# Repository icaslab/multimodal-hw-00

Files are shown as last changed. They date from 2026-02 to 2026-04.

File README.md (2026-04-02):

⚔️ Work in Progress: This repository is under active development. Please do not make changes. ⚔️

### Multimodal Transcutaneous Monitor Hardware (PtcO₂ / PtcCO₂ / SpO₂ / BIA)

### Key Specs
- **MCU:** STM32WB55RGV6 (dual-core Cortex-M4/M0+, BLE 5.0) — VFQFPN68
- **Analog Front End:** ADPD7000 (optical + bio-impedance/BIA sensing) — 36-ball WLCSP, 0.4mm pitch
- **Storage:** S25FL512S — 512 Mb QuadSPI Flash (5×5 BGA)
- **Power Input:** USB-C (2.0) or 3.7V Li-Po with integrated battery charging

### Sensors / Peripherals
- **BME280** (Temp/Humidity/Pressure) over I²C (`0x76`)
- **ADXL367** (Accelerometer) over I²C (`0x53`)

### Power Management
- **MAX20345** single-chip PMIC (WLP-56, 0.4mm pitch) with:
  - Integrated Li-Po charger (ISET = 10kΩ → ~200mA charge current)
  - NTC thermistor monitoring (SEMITEC 103AT-11)
  - **Buck 2:** 1.8V analog rail (`1V8A`) — low-noise AFE supply
  - **Buck 3:** 3.3V digital rail (`3V3D`) — MCU + digital peripherals
  - **Buck-Boost:** 5.0V LED drive domain (`5V_LED`) — optical front end
  - **LDO 1:** 1.8V digital rail (`1V8D`)
  - **LDO 2:** 3.3V LED rail (`3V3_LED`)
  - **LDO 3:** Alternative output (`L3OUT`)
  - **Load Switches:** LSW1, LSW2 not used either 
  - Buck 1 unused — disabled via I²C

### PCB
- **Stackup:** 6-layer HDI (Sig+Pwr / GND / Sig / PwR / GND / Sig)
- **HDI:** Stacked/staggered µVias (100µm laser drill, 250µm pad, via-in-pad with epoxy fill + cap plating)

### Repository Organization
- `Datasheets/`  
  - Find component datasheets here.

### Schematic Sheets
- `00-multimodal-coversheet.SchDoc`
- `01-multimodal-powersupply.SchDoc`
- `04-multimodal-flash.SchDoc`
- `05-multimodal-analogfrontend.SchDoc`
- `06-multimodal-analogfrontend-PPG.SchDoc`
- `07-multimodal-microcontroller.SchDoc`
- `08-multimodal-microcontroller-oscillators.SchDoc`
- `10-multimodal-microcontroller-rf.SchDoc`
- `11-multimodal-combined-sensor.SchDoc`
- `12-multimodal-accelerometer.SchDoc`
- `13-multimodal-connections.SchDoc`

```text
⠀⠀⢸⡿⢦⣄⠀⢀⣠⣴⣶⠀⠀⠀⠀⠀⠀⠀⠀⠀⠀⠀⠀⠀⠀
⠀⠀⠘⣷⠀⠉⠛⠛⠉⢰⡇⠀⠀⠘⣷⣦⣾⡇⠀⠀⠀⠀⠀⠀⠀
⠀⢀⣰⠿⠀⠀⠀⠀⠀⢿⡁⠀⢀⣴⣿⣿⣿⣶⡄⠀⠀⠀⠀⠀⠀
⣴⣿⣁⡀⠀⠀⠀⠀⠀⠀⠻⣦⡀⠀⠀⢿⠃⠀⢀⣤⡀⠀⠀⠀⠀
⠀⠈⠉⠛⣿⡀⠀⣰⠟⠛⠛⠛⠛⠀⠀⠀⠀⣠⡾⢻⡇⠀⠀⠀⠀
⠀⠀⠀⠀⠈⣷⣼⠏⠀⠀⠀⢻⣟⠻⠿⢶⡾⠋⠀⢸⡇⠀⠀⠀⠀
⠀⠀⠀⠀⠀⠘⠃⠀⣴⠀⠀⠈⢻⣆⠀⠀⠀⠀⠀⠀⠻⢶⣤⣀⠀
⠀⠀⠀⠀⠀⠘⢷⣾⣿⣤⣄⠀⢈⣿⠀⠀⠀⠀⠀⠀⠀⢀⣉⣿⠿
⠀⠀⠀⠀⠀⢀⣾⠿⣿⡏⠉⢠⣾⠃⠀⠀⠀⠀⠀⢀⣾⠛⠋⠁⠀
⠀⠀⠀⠀⠀⠀⠀⠀⠙⠃⠀⣿⡷⠿⠟⠛⢿⣦⡀⢸⡇⠀⠀⠀⠀
⠀⠀⠀⠀⠀⠀⠀⠀⠀⠀⠀⠀⠀⠀⠀⠀⠀⠀⠀⠙⢿⣿⠃⠀⠀
⠀⠀⠀⠀⠀⠀⠀⠀⠀⠀⠀⠀⠀⠀⠀⠀⠀⠀⠀⠀⠀⠉⠀⠀⠀
```

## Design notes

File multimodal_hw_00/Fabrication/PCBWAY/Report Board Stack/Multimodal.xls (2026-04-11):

Board Stack Report
Stack Up |  | Layer Stack
Layer | Board Layer Stack | Name | Material | Thickness | Constant | Dk
1 |  | Top Overlay |  | 0mil
2 |  | Top Solder | Solder Resist | 0.4mil | 3.5 | 3.5
3 |  | L1_TOP | CF-001 | 0.689mil
4 |  | Dielectric 2 | PP-006 | 4.705mil | 4.45 | 4.45
5 |  | L2_GND | CF-004 | 1.378mil
6 |  | Dielectric 4 | PP-006 | 9.055mil | 4.6 | 4.6
7 |  | L3_Signal | CF-004 | 1.378mil
8 |  | Dielectric 6 | PP-006 | 5.118mil | 4.45 | 4.45
9 |  | Dielectric 1 | FR-4 | 0mil | 4.45 | 4.45
10 |  | Dielectric 7 | PP-006 | 5.118mil | 4.45 | 4.45
11 |  | L4_PWR | CF-004 | 1.378mil
12 |  | Dielectric 5 | PP-006 | 9.055mil | 4.6 | 4.6
13 |  | L5_GND | CF-004 | 1.378mil
14 |  | Dielectric 3 | PP-006 | 4.705mil | 4.45 | 4.45
15 |  | L6_BOTTOM | CF-001 | 0.689mil
16 |  | Bottom Solder | Solder Resist | 0.4mil | 3.5 | 3.5
17 |  | Bottom Overlay |  | 0mil
 | Height : 45.446mil

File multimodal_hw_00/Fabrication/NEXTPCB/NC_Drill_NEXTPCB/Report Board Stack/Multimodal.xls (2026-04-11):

Board Stack Report
Stack Up |  | Layer Stack
Layer | Board Layer Stack | Name | Material | Thickness | Constant | Dk
1 |  | Top Overlay |  | 0mil
2 |  | Top Solder | Solder Resist | 0.4mil | 3.5 | 3.5
3 |  | L1_TOP | CF-001 | 0.453mil
4 |  | Dielectric 2 | PP-006 | 3.032mil | 4 | 4
5 |  | L2_GND | CF-004 | 0.453mil
6 |  | Dielectric 4 | PP-006 | 3.032mil | 4 | 4
7 |  | L3_Signal | CF-004 | 0.453mil
8 |  | Dielectric 1 | FR-4 | 46.339mil | 4 | 4
9 |  | L4_PWR | CF-004 | 0.453mil
10 |  | Dielectric 5 | PP-006 | 3.032mil | 4 | 4
11 |  | L5_GND | CF-004 | 0.453mil
12 |  | Dielectric 3 | PP-006 | 3.032mil | 4 | 4
13 |  | L6_BOTTOM | CF-001 | 0.453mil
14 |  | Bottom Solder | Solder Resist | 0.4mil | 3.5 | 3.5
15 |  | Bottom Overlay |  | 0mil
 | Height : 61.985mil

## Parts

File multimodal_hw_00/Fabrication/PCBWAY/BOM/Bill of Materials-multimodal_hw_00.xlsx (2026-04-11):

Line # | Name | Description | Designator | Quantity | Manufacturer 1 | Manufacturer Part Number 1 | Manufacturer Lifecycle 1 | Supplier 1 | Supplier Part Number 1 | Supplier Unit Price 1 | Supplier Subtotal 1
 | ANT016008LCS2442MA2 | TDK - ANT016008LCS2442MA2 - Chip Antenna, ISM, 2.442 GHz, 50 Ohm, 1.6mm x 0.8mm x 0.4mm | AE1 | 1 | TDK | ANT016008LCS2442MA2 | Volume Production | DigiKey | 445-172405CT-ND | 0.61 | 0.61
 | C1005X5R1V105K050BC | CAP CER 1UF 35V X5R 0402 | C1, C8, C16, C18, C23, C24, C50 | 7 | TDK | C1005X5R1V105K050BC | Volume Production | DigiKey | 445-9073-1-ND | 0.071 | 0.71
 | C1005X5R1A475K050BC | CAP CER 4.7UF 10V X5R 0402 | C2, C38 | 2 | TDK | C1005X5R1A475K050BC | Volume Production | Digi-Key | 445-13820-1-ND
 | GRM188R61A226ME15D | CAP CER 22UF 10V X5R 0603 | C3, C4, C5, C9, C10, C13, C14 | 7 | Murata | GRM188R61A226ME15D | Volume Production | Avnet | GRM188R61A226ME15D | 0.01867 | 74.68
 | CL05A225KO5NQNC | CAP CER 2.2UF 16V X5R 0402 | C6, C11, C12, C15, C64 | 5 | Samsung Electro-Mechanics | CL05A225KO5NQNC | Volume Production | Avnet | CL05A225KO5NQNC | 0.0264 | 264
 | C1005X7R1H104K050BB | CAP CER 0.1UF 50V X7R 0402 | C7, C17, C26, C29, C30, C31, C33, C35, C36, C37, C40, C41, C42, C48, C51, C52, C53, C55, C57, C58, C60, C61 | 22 | TDK | C1005X7R1H104K050BB | Volume Production | DigiKey | 445-5932-1-ND | 0.041 | 0.902
 | GRM155R60J474KE19D | CAP CER 0.47UF 6.3V X5R 0402 | C21, C22, C25, C27 | 4 | Murata | GRM155R60J474KE19D | Not Recommended for New Design | Avnet | GRM155R60J474KE19D | 0.00818 | 81.8
 | 0402W106M6R3HI | CAP SMD,0402,X5R,10UF,20%,6.3V | C28, C32, C54, C56 | 4
 | GRM155R61A106ME11D | CAP CER 10UF 10V X5R 0402 | C34, C47, C49 | 3 | Murata | GRM155R61A106ME11D | Volume Production | DigiKey | 490-GRM155R61A106ME11DCT-ND | 0.013 | 0.13
 | CGA2B2C0G1H101J050BA | CAP CER 100PF 50V C0G 0402 | C43 | 1 | TDK | CGA2B2C0G1H101J050BA | Volume Production | DigiKey | 445-5596-1-ND | 0.1 | 0.1
 | CGA2B2C0G1H120J050BA | CAP CER 12PF 50V C0G 0402 | C45, C46 | 2 | TDK | CGA2B2C0G1H120J050BA | Volume Production | DigiKey | 445-5585-1-ND | 0.1 | 0.2
 | CGA2B2C0G1H101J050BA | CAP CER 100PF 50V C0G 0402 | C62 | 1 | TDK | CGA2B2C0G1H101J050BA | Volume Production | DigiKey | 445-5596-1-ND | 0.1 | 0.1
 | USBLC6-2SC6 | ESD Protection for USB 2.0 High Speed | CR1 | 1 | STMicroelectronics | USBLC6-2SC6 | Volume Production | Avnet | USBLC6-2SC6 | 0.07203 | 216.09
 | ESD9X5.0ST5G | TVS DIODE 5VWM 12.3VC SOD923 | CR3 | 1 | onsemi | ESD9X5.0ST5G | Volume Production | Avnet | ESD9X5.0ST5G | 0.01716 | 137.28
 | DESD3V3S1BL-7B | TVS DIODE 3.3V 7V DFN1006-2 | D1 | 1 | Diodes Inc. | DESD3V3S1BL-7B | Volume Production | DigiKey | DESD3V3S1BL-7BDICT-ND | 0.24 | 0.24
 | SFH 2703 | SENSOR PHOTODIODE 940NM 2SMD | D3, D10, D11 | 3 | Osram | SFH 2703 | Volume Production | Avnet | Q65112A8147 | 0.50312 | 1509.36
 | LXZ1-PR01 | LED LUXEON Z RYL BLUE 450NM 2SMD | D4, D5 | 2 | Lumileds | LXZ1-PR01 | Volume Production | DigiKey | 1416-1058-1-ND | 3.32 | 6.64
 | 019-141-411-R | PHOTODIODE RED MICRO SMT | D6 | 1 | Advanced Photonix | 019-141-411-R |  | DigiKey | 209-019-141-411-RCT-ND | 1.96 | 1.96
 | S15193 | PHOTODIODE PIN 380 NM-1000 NM 20V 0.64 A/W SMD | D7 | 1 |  |  |  | Hamamatsu
 | CT DBLP31.12-6C5D-56-J6Q4 | LED GREEN CLEAR SMD Green 536nm LED Indication - Discrete 2.3V 3-SMD, No Lead | D8 | 1 | Osram | CT DBLP31.12-6C5D-56-J6Q4 | Volume Production | Avnet | Q65112A4607
 | SFH 7015 | Multi-Color LEDs Red / IR LED 655nm / 940nm | D9 | 1 | Osram | SFH 7015 | Obsolete | Avnet | Q65113A4161 | 0.3798 | 1899
 | RB521S30T1G | DIODE SCHOTTKY 30V 200MA SOD523 | D12 | 1 |  |  |  | Hamamatsu
 | Orange | LED ORANGE CLEAR 0603 SMD | D13 | 1 | Lite-On | LTST-C191KFKT | Volume Production | DigiKey | 160-1445-1-ND | 0.11 | 0.11
 | MAF1608GAD601CT000 | FERRITE BEAD 120 OHM 0603 1LN | FB1, FB2, FB3, FB4 | 4 | TDK | MAF1608GAD601CT000 | Volume Production | Newark | MAF1608GAD601CT000 | 0.185 | 1.85
 | MFBA3V1608K-601-R | FERRITE BEAD 600 OHM 0603 1LN | FB5 | 1 | Eaton | MFBA3V1608K-601-R | Volume Production | DigiKey | 283-MFBA3V1608K-601-RCT-ND | 0.1 | 0.1
 | FTSH-105-01-F-DV-P-TR | Connector Header Surface Mount 10 position 0.050" (1.27mm) | J1 | 1
 | TH-Connector | Power Connector | J2 | 1
 | 2171790001 | Universal Serial Bus (USB) Shielded I/O Receptacle, Type C, Right-Angle, Top Mount, Surface Mount, Single Row, 16 Circuits, Gold (Au) Plating | J3 | 1
 | battery_connection |  | J4 | 1
 | U.FL-R-SMT(10) | CONN U.FL RCPT STR 50 OHM SMD | J5 | 1 | HIROSE ELECTRIC | U.FL-R-SMT(10) | Volume Production | DigiKey | H9161CT-ND | 1.29 | 1.29
 | electrode | one pad opening | J6, J7, J8, J9 | 4
 | SEMITEC 103AT-11 | NTC THERMISTOR 10KOHM 1% | J11 | 1
 | MLG0603P1N8CT000 | FIXED IND 1.8NH 700MA 100MOHM SM | L5 | 1 | TDK | MLG0603P1N8CT000 | Volume Production | DigiKey | 445-172430-1-ND | 0.1 | 0.1
 | MHQ0603P2N9ST000 | FIXED IND 2.9NH 450MA 300MOHM SM | L6 | 1 | TDK | MHQ0603P2N9ST000 | Volume Production | DigiKey | 445-16842-6-ND | 0.3 | 0.3
 | DFE201612E-2R2M=P2 | 2.2 µH Shielded Drum Core, Wirewound Inductor 1.8 A 116mOhm Max 0806 (2016 Metric) | L7, L9, L10 | 3
 | RMCF0402FT93K1 | RES 93.1K OHM 1% 1/16W 0402 | R1, R12 | 2 | Stackpole Electronics | RMCF0402FT93K1 | Volume Production | DigiKey | RMCF0402FT93K1CT-ND | 0.005 | 0.05
 | RMCF0402FT220K | RES 220K OHM 1% 1/16W 0402 | R2, R13 | 2 | Stackpole Electronics | RMCF0402FT220K | Volume Production | DigiKey | RMCF0402FT220KCT-ND | 0.005 | 0.05
 | RMCF0603ZT0R00 | RES 0 OHM JUMPER 1/10W 0603 | R3, R10, R17, R25, R34, R35, R39 | 7 | Stackpole Electronics | RMCF0603ZT0R00 | Volume Production | DigiKey | RMCF0603ZT0R00CT-ND | 0.006 | 0.06
 | RMCF0402FT100K | RES 100K OHM 1% 1/16W 0402 | R5, R8, R9, R15, R19, R24 | 6 | Stackpole Electronics | RMCF0402FT100K | Volume Production | DigiKey | RMCF0402FT100KCT-ND | 0.005 | 0.05
 | RMCF0402FT10K0 | RES 10K OHM 1% 1/16W 0402 | R6, R11 | 2 | Stackpole Electronics | RMCF0402FT10K0 | Volume Production | DigiKey | RMCF0402FT10K0CT-ND | 0.005 | 0.05
 | RMCF0603JG10K0 | RES 10K OHM 5% 1/10W 0603 | R7 | 1 | Stackpole Electronics | RMCF0603JG10K0 | Volume Production | DigiKey | 738-RMCF0603JG10K0CT-ND | 0.1 | 0.1
 | RMCF0603JG100K | RES 100K OHM 5% 1/10W 0603 | R21 | 1 | Stackpole Electronics | RMCF0603JG100K | Volume Production | DigiKey | RMCF0603JG100KCT-ND | 0.1 | 0.1
 | RMCF0402JT220R | RES 220 OHM 5% 1/16W 0402 | R22 | 1 | Stackpole Electronics | RMCF0402JT220R | Volume Production | DigiKey | RMCF0402JT220RCT-ND | 0.1 | 0.1
 | ERA-2AEB512X | RES SMD 5.1K OHM 0.1% 1/16W 0402 | R28, R33 | 2 | Panasonic | ERA2AEB512X | Volume Production | Arrow Electronics | ERA-2AEB512X | 0.0452 | 452
 | RMCF0402FT4K70 | RES 4.7K OHM 1% 1/16W 0402 | R31, R32 | 2 | Stackpole Electronics | RMCF0402FT4K70 | Volume Production | Digi-Key | RMCF0402FT4K70CT-ND
 | RMCF0402FT10R0 | RES 10 OHM 1% 1/16W 0402 | R36, R37 | 2 | Stackpole Electronics | RMCF0402FT10R0 | Volume Production | DigiKey | RMCF0402FT10R0CT-ND | 0.006 | 0.06
 | RMCF0402ZT0R00 | RES 0 OHM JUMPER 1/16W 0402 | R38 | 1 | Stackpole Electronics | RMCF0402ZT0R00 | Volume Production | DigiKey | RMCF0402ZT0R00CT-ND | 0.1 | 0.1
 | S0951-46R | RFI SHIELD CLIP MINI TIN SMD | SC1, SC2 | 2 | Harwin | S0951-46R | Volume Production | DigiKey | 952-2669-1-ND | 0.19 | 0.38
 | MS190-10C | RF SHLD COVER 0.563"X0.764" SNAP | SH1 | 1 | Masach Tech | MS190-10C | Volume Production | DigiKey | 2333-MS190-10C-ND | 1.12 | 1.12
 | NANOT 240 AS | SWITCH TACTILE SPST-NO 0.02A 15V | SW1, SW2 | 2 |  |  |  | Future Electronics | 2189518
 | MAX20345BEWN+T | PMIC with Ultra-Low IQ Voltage Regulators, Buck-Boost for Optical Sensing and Charger for Small Lithium Ion Systems | U1 | 1 | Analog Devices | MAX20345BEWN+T | Volume Production | DigiKey | 505-MAX20345BEWN+TTR-ND
 | S25FL512SAGBHEA10 | FLASH - NOR Memory IC 512Mbit SPI - Quad I/O 133 MHz 24-BGA (6x8) | U3 | 1
 | ADXL367BCCZ-RL7 | Accelerometer X, Y, Z Axis ±2g, 4g, 8g 6.25Hz ~ 200Hz 12-LGA (2.2x2.3) | U4 | 1 | Analog Devices | ADXL367BCCZ-RL7 | Volume Production | DigiKey | 505-ADXL367BCCZ-RL7CT-ND
 | ADPD7000BCBZR7 | Multimodal Sensor Front End | U5 | 1
 | STM32WB55RGV6 | Ultra-low-power dual core Arm Cortex-M4 MCU 64 MHz, Cortex-M0+ 32 MHz with 1 Mbyte of Flash memory, Bluetooth LE 5.4, 802.15.4, Zigbee, Thread, Matter, USB, LCD, AES-256 | U6 | 1
 | MLPF-WB55-01E3 | 2.4 GHz Matched filter companion chip for STM32WB55Cx and STM32WB55Rx | U7 | 1 | STMicroelectronics | MLPF-WB55-01E3 | Volume Production | DigiKey | 497-19088-1-ND | 0.37 | 0.37
 | BME280 | SENSOR PRESSURE HUMIDITY TEMP Humidity, Pressure, Temperature 0 ~ 100% RH I2C, SPI ±3% 1 s Surface Mount | U8 | 1
 | 32MHz | CRYSTAL 32MHZ 8PF 60R SMD | XO1 | 1 |  |  |  | Digi-Key | 644-1373-1-ND
 | ECS-327-9-12R-C-TR | Crystal 0.032768MHz ±10ppm (Tol) 9pF Flexural 70000Ohm Automotive 2-Pin Ultra Mini-CSMD T/R | XO2 | 1 | ECS International | ECS-.327-9-12R-C-TR | Volume Production | DigiKey | XC2744CT-ND | 0.75 | 0.75

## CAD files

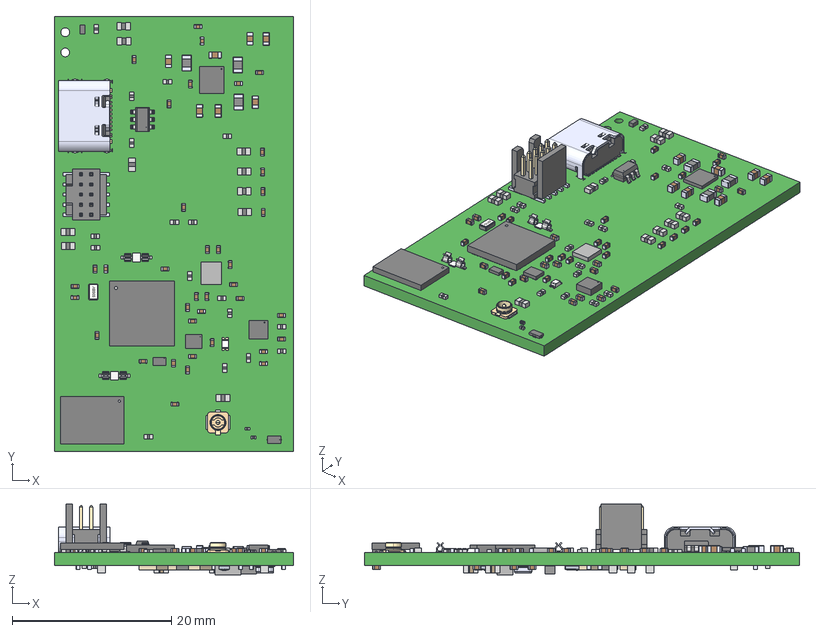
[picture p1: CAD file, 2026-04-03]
multimodal_hw_00/3D-board/Multimodal.step
30.0 x 54.6 x 8.87 mm
STA_RMCF0402_STP x 20
s0951-46 x 2
DFE201612E-2R2M=P2 x 3
bigPin x 2
Extruded x 2
ABS06-32.768KHZ-9-1-T--3DModel-STEP-400430
MLPF-WB55-01E3_STM
U.FL-R-SMT(10)--3DModel-STEP-56544
LTST-C191KRKT
CTDBLP3112-6C5D-56-J6Q4_OSR
Pins
LUXEON Z InGaN Direct Color 0660 x 2
SOT23-6L_STM
QFN_2442MA2_TDK

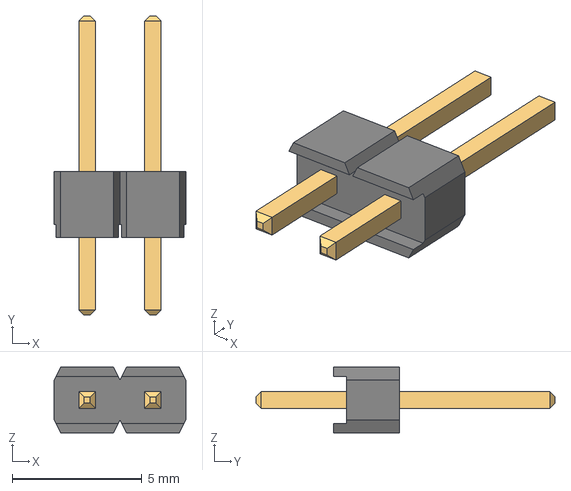
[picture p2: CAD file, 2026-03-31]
multimodal_hw_00/3D-models/STP_61300211121_rev1.stp
5.08 x 11.5 x 2.54 mm
6130xx11121_PIN x 2

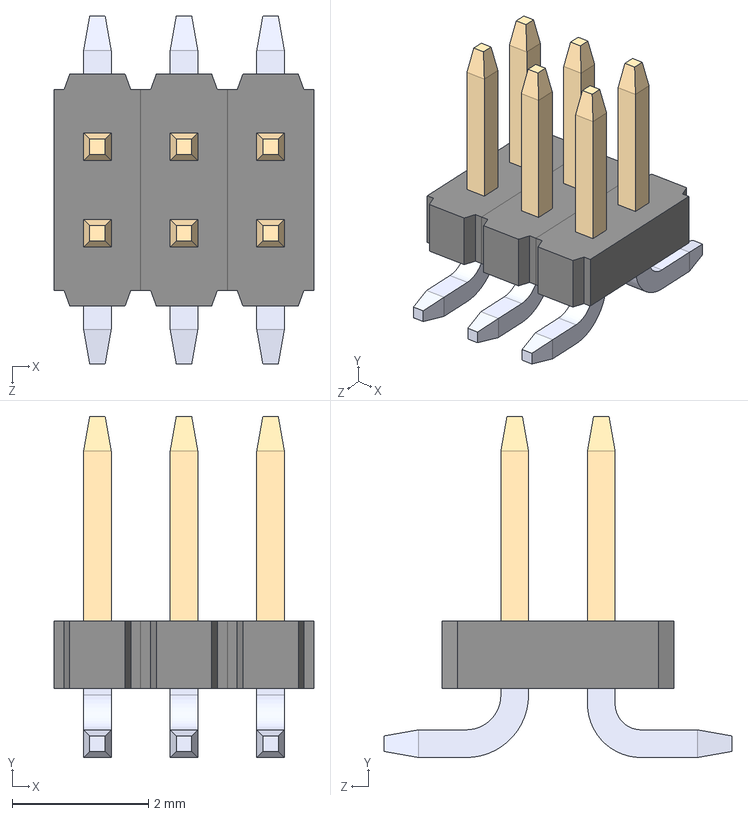
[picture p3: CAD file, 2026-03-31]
multimodal_hw_00/3D-models/GRPB032VWQS-RC--3DModel-STEP-269445.STEP
3.81 x 5.00 x 5.11 mm
GRPB012VWQS-RC_GRPB032VWQS-RC
Pin - Gold and Tin_RC x 3
Pin - Gold and Tin x 3

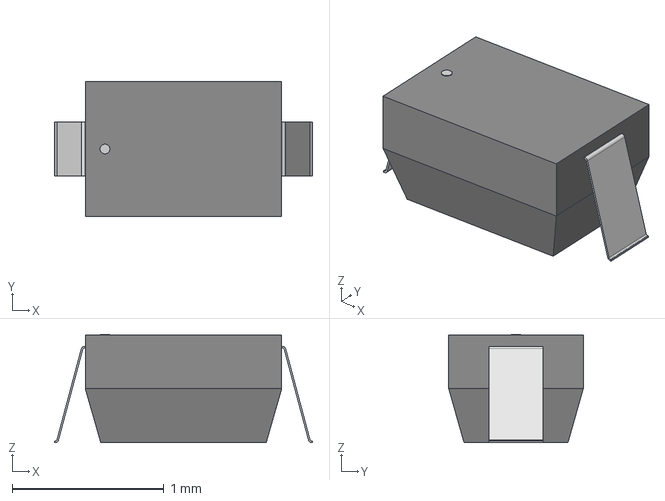
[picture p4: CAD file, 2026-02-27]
multimodal_hw_00/3D-models/SOD-523_STM.step
1.70 x 0.888 x 0.714 mm

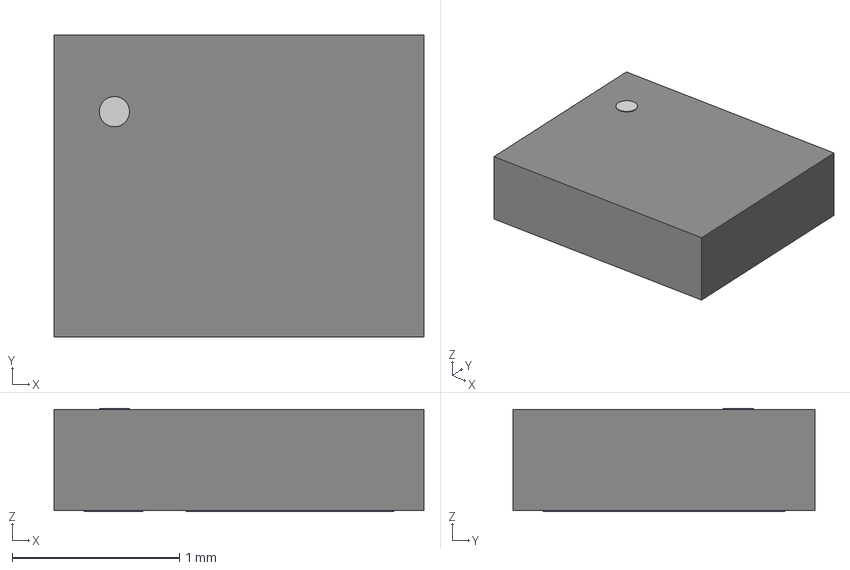
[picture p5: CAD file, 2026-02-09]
multimodal_hw_00/3D-models/CTDBLP3112-6C5D-56-J6Q4_OSR.step
2.21 x 1.80 x 0.616 mm

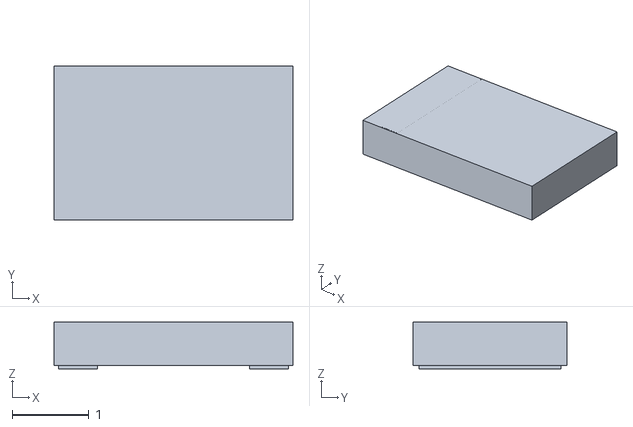
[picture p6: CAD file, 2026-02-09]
multimodal_hw_00/3D-models/LED_SFH2703_OSR.stl
3.11 x 2.01 x 0.612

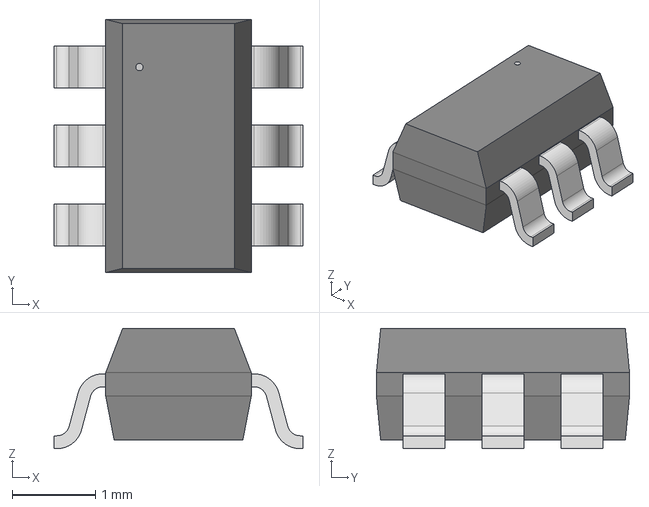
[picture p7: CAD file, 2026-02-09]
multimodal_hw_00/3D-models/SOT23-6L_STM.step
3.00 x 3.05 x 1.45 mm

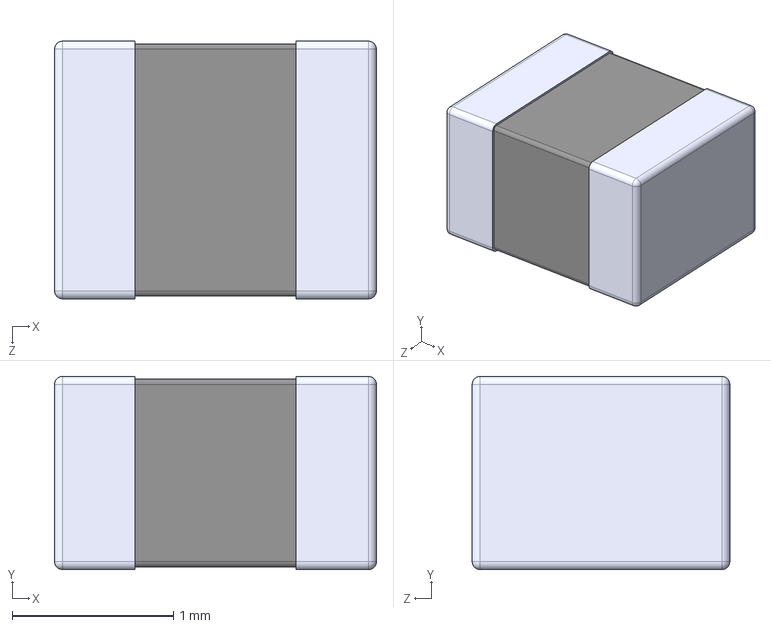
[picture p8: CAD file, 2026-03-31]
multimodal_hw_00/3D-models/DFE201612E-2R2M=P2.STEP
2.00 x 1.20 x 1.60 mm

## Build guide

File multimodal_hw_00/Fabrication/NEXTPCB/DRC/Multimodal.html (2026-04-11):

Altium

# Design Rule Verification Report

Date: | | 4/11/2026
Time: | | 5:32:05 PM
Elapsed Time: | | 00:00:02
Filename: | | C:\Users\isili\OneDrive\Desktop\multimodal-hw-00\multimodal_hw_00\multimodal_hw_00\Multimodal.PcbDoc

Warnings: | | 0
Rule Violations: | | 0
PCB Health Issues: | | 7

## Summary

Warnings | Count
Total | 0

Rule Violations | Count
Clearance Constraint (Gap=0mil) (Keepout),(All) | 0
Clearance Constraint (Gap=3mil) (IsMicroVia),(All) | 0
Clearance Constraint (Gap=3mil) (IsBlindVia),(All) | 0
Clearance Constraint (Gap=5mil) (All),(All) | 0
Short-Circuit Constraint (Allowed=No) (All),(All) | 0
Un-Routed Net Constraint ( (All) ) | 0
Modified Polygon (Allow modified: No), (Allow shelved: No) | 0
Width Constraint (Min=4mil) (Max=71497.938mil) (Preferred=4mil) (All) | 0
Width Constraint (Min=6mil) (Max=1000mil) (Preferred=6mil) (All) | 0
Width Constraint (Min=3mil) (Max=50mil) (Preferred=10mil) (All) | 0
Width Constraint (Min=10mil) (Max=1000mil) (Preferred=12mil) (All) | 0
Width Constraint (Min=10mil) (Max=1000mil) (Preferred=20mil) (All) | 0
Width Constraint (Min=10mil) (Max=1000mil) (Preferred=10mil) (All) | 0
Routing Topology Rule(Topology=Shortest) (All) | 0
Power Plane Connect Rule(Direct Connect )(Expansion=20mil) (Conductor Width=10mil) (Air Gap=10mil) (Entries=4) (InPadClass('PowerPads')) | 0
Power Plane Connect Rule(Relief Connect )(Expansion=11.811mil) (Conductor Width=4mil) (Air Gap=4mil) (Entries=4) (All) | 0
Minimum Annular Ring (Minimum=2mil) (IsVia) | 0
Hole Size Constraint (Min=3.937mil) (Max=248.031mil) (All) | 0
Hole To Hole Clearance (Gap=7.874mil) (All),(All) | 0
Minimum Solder Mask Sliver (Gap=0mil) (IsVia),(All) | 0
Minimum Solder Mask Sliver (Gap=2mil) (All),(All) | 0
Silk To Solder Mask (Clearance=2mil) (IsPad),(All) | 0
Silk to Silk (Clearance=5mil) (All),(All) | 0
Net Antennae (Tolerance=0mil) (All) | 0
Board Clearance Constraint (Gap=0mil) (All) | 0
Matched Lengths(Tolerance=10mil) (InNetClass('FLASH_QUAD_SPI')) | 0
Height Constraint (Min=0mil) (Max=71497.938mil) (Prefered=500mil) (All) | 0
Total | 0

PCB Health Issues | Count
Duplicate Component Designators | 3
Slots Hole Size > Length | 4
Total | 7

## Rule Violations

## PCB Health Issues

Duplicate Component Designators

Duplicated Designators: SMT Small Component GND-TESTPOINT_S (5414.378mil,2953.086mil) on L1_TOP

Duplicated Designators: SMT Small Component GND-TESTPOINT_S (5073.903mil,4205.428mil) on L1_TOP

Duplicated Designators: SMT Small Component GND-TESTPOINT_S (5586.785mil,4291.267mil) on L1_TOP

Back to top

Slots Hole Size > Length

Slot holes size > length: Pad J3-15(4777.846mil,4386.574mil) on Multi-Layer

Slot holes size > length: Pad J3-16(4777.846mil,4046.416mil) on Multi-Layer

Slot holes size > length: Pad J3-13(4620.365mil,4386.574mil) on Multi-Layer

Slot holes size > length: Pad J3-14(4620.365mil,4046.416mil) on Multi-Layer

Back to top

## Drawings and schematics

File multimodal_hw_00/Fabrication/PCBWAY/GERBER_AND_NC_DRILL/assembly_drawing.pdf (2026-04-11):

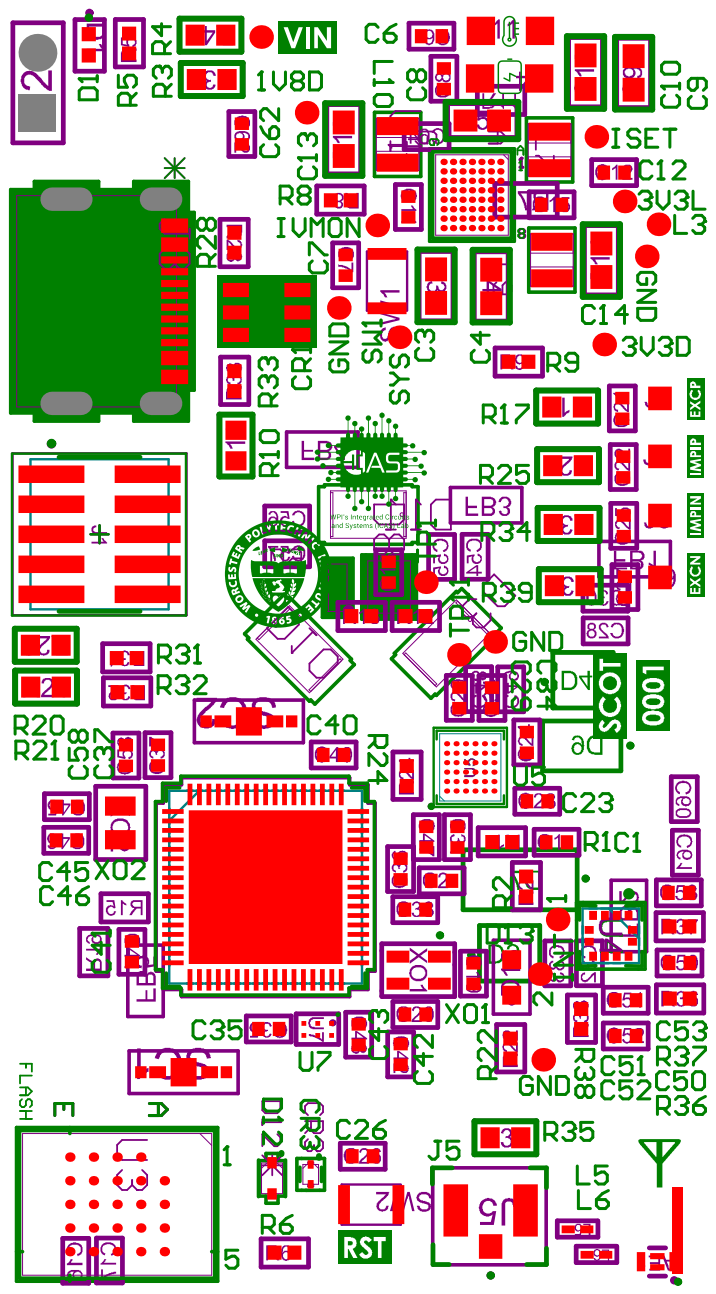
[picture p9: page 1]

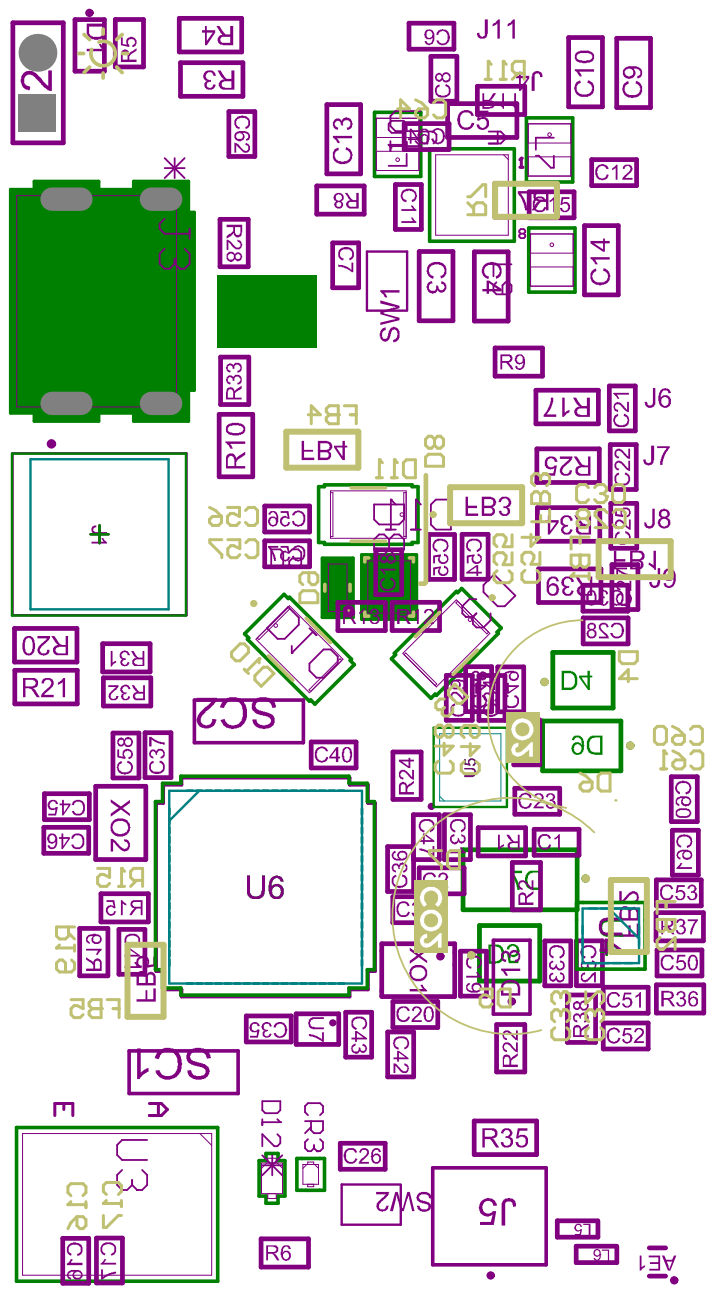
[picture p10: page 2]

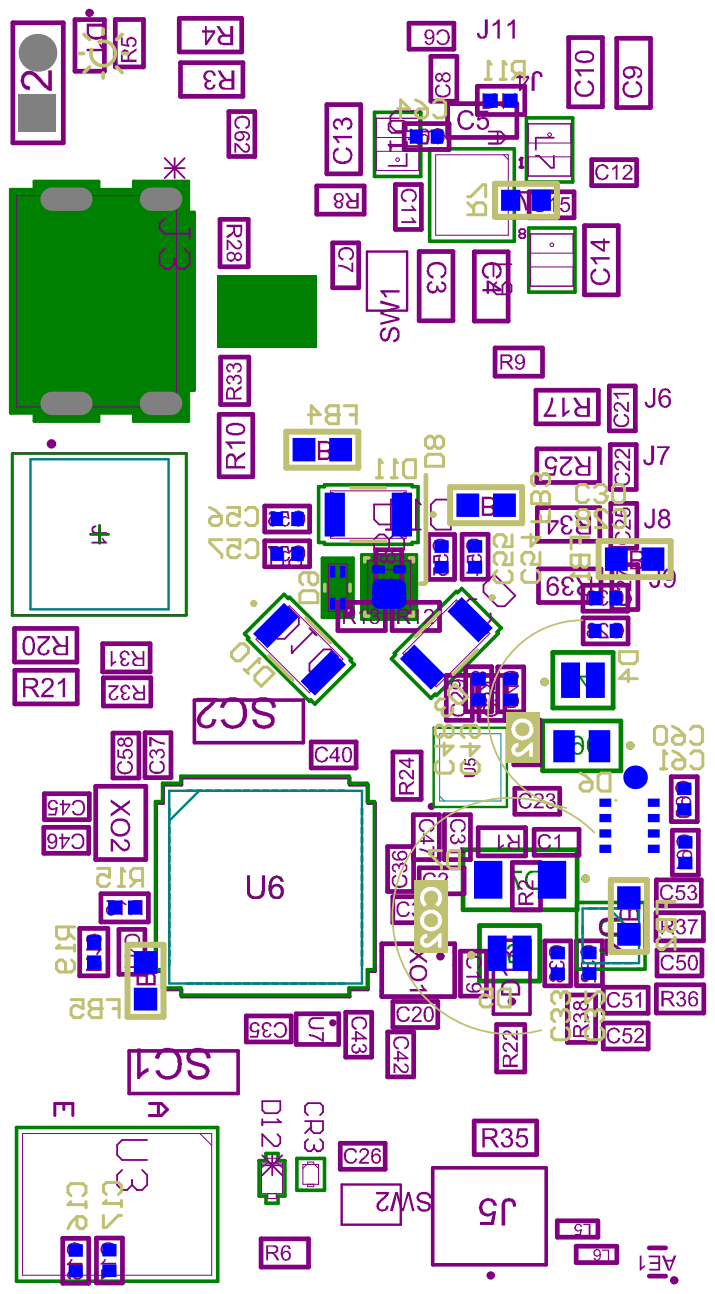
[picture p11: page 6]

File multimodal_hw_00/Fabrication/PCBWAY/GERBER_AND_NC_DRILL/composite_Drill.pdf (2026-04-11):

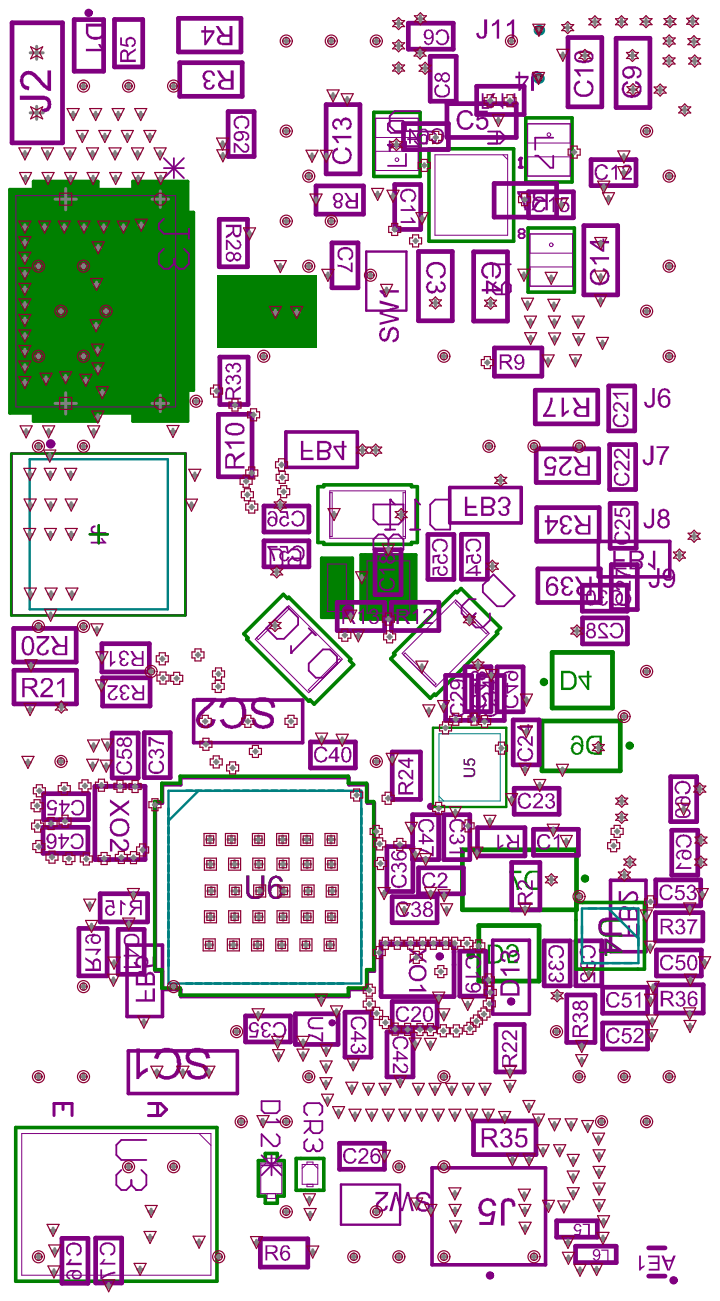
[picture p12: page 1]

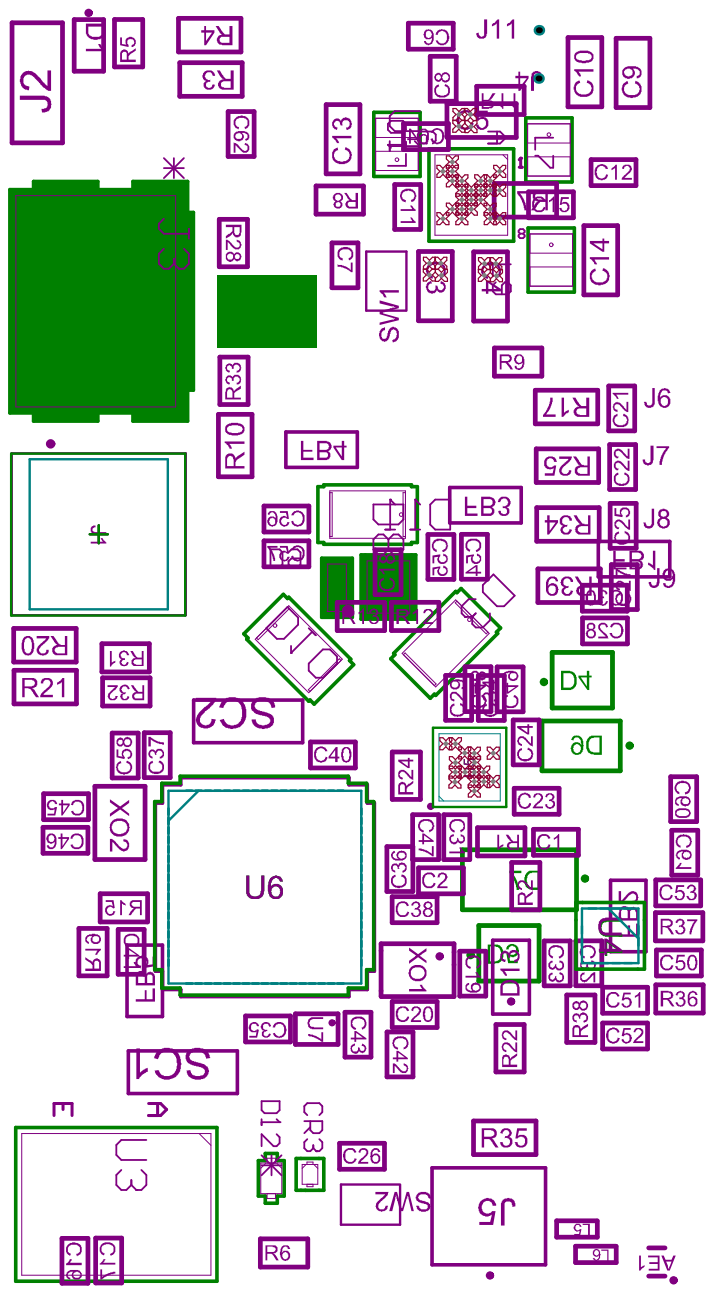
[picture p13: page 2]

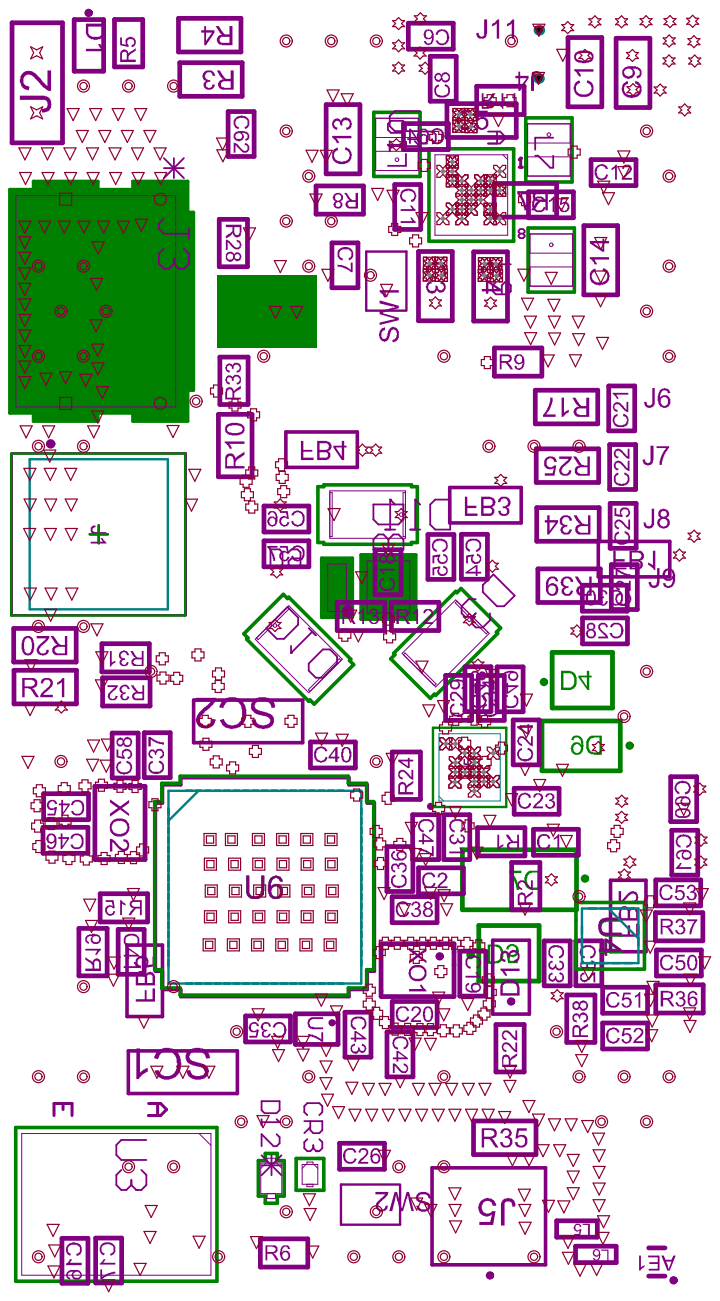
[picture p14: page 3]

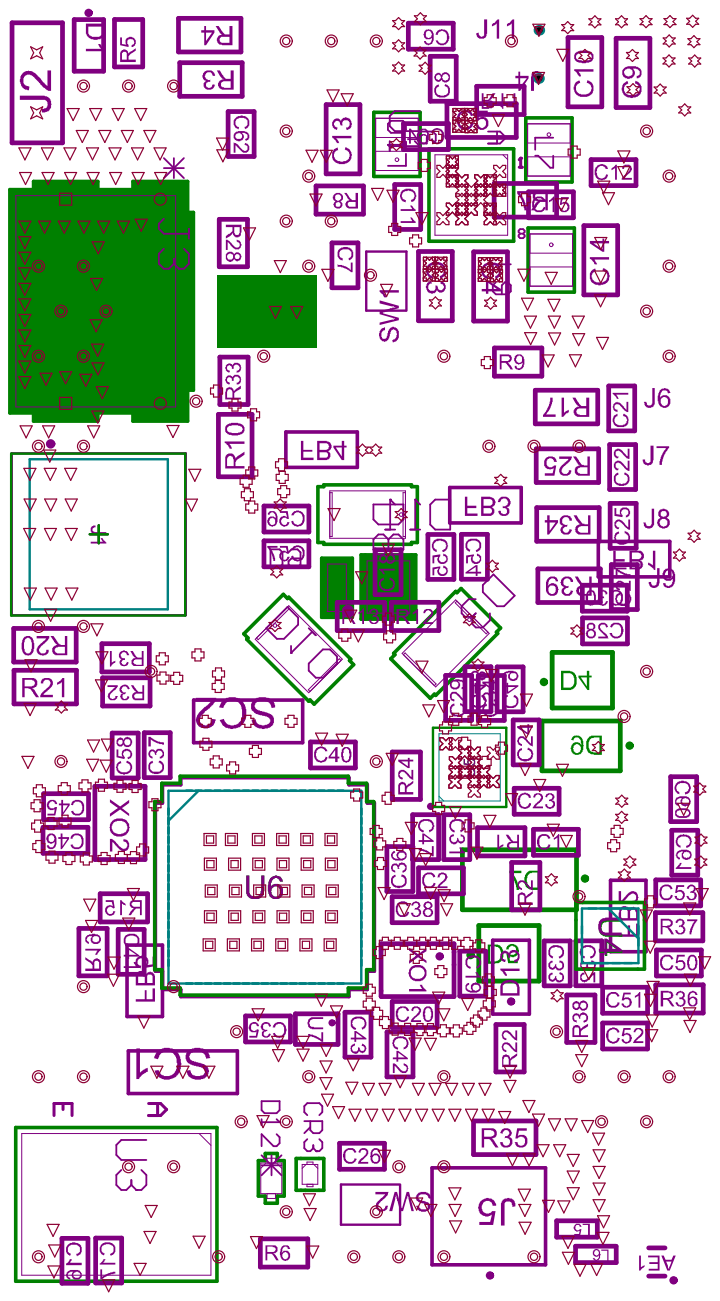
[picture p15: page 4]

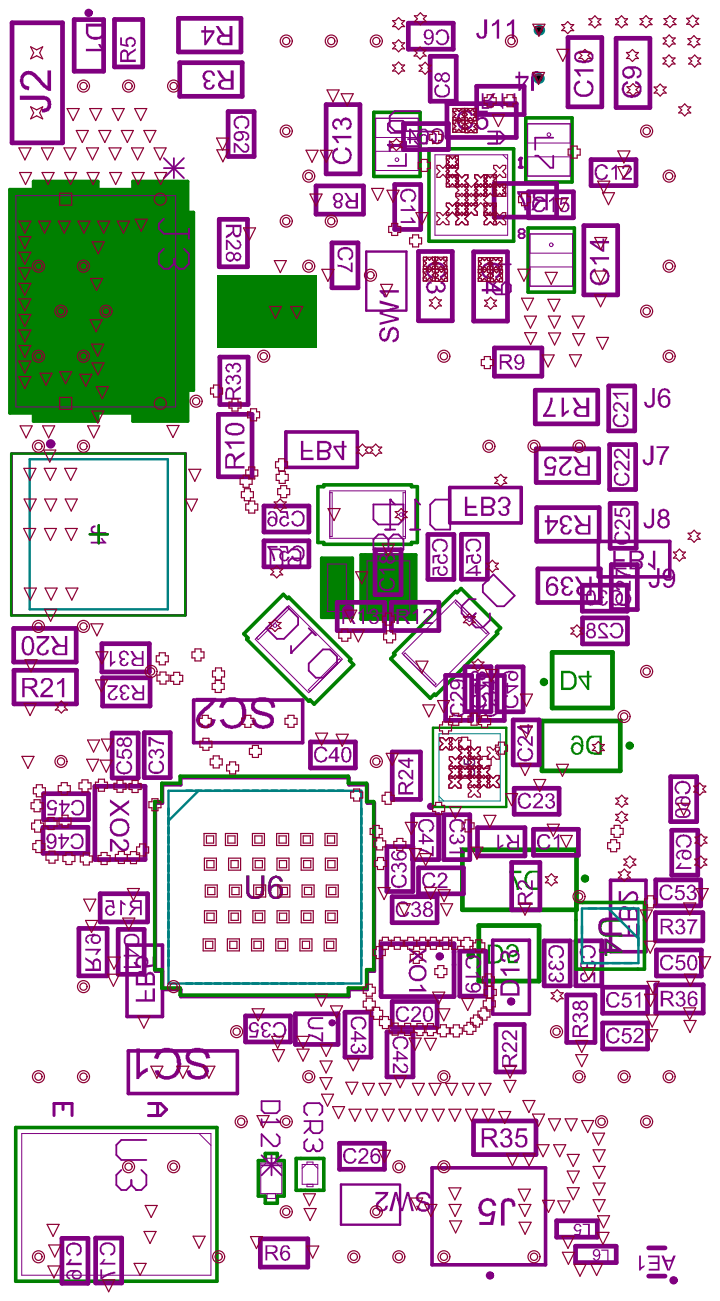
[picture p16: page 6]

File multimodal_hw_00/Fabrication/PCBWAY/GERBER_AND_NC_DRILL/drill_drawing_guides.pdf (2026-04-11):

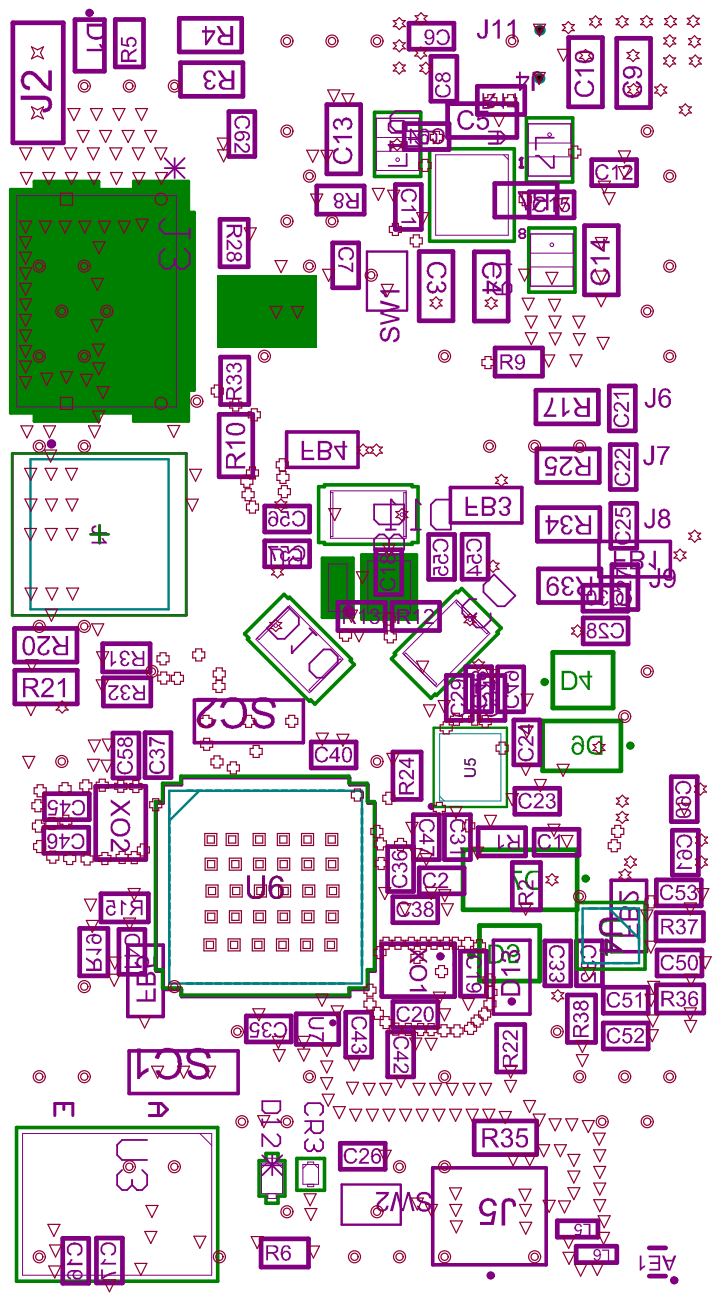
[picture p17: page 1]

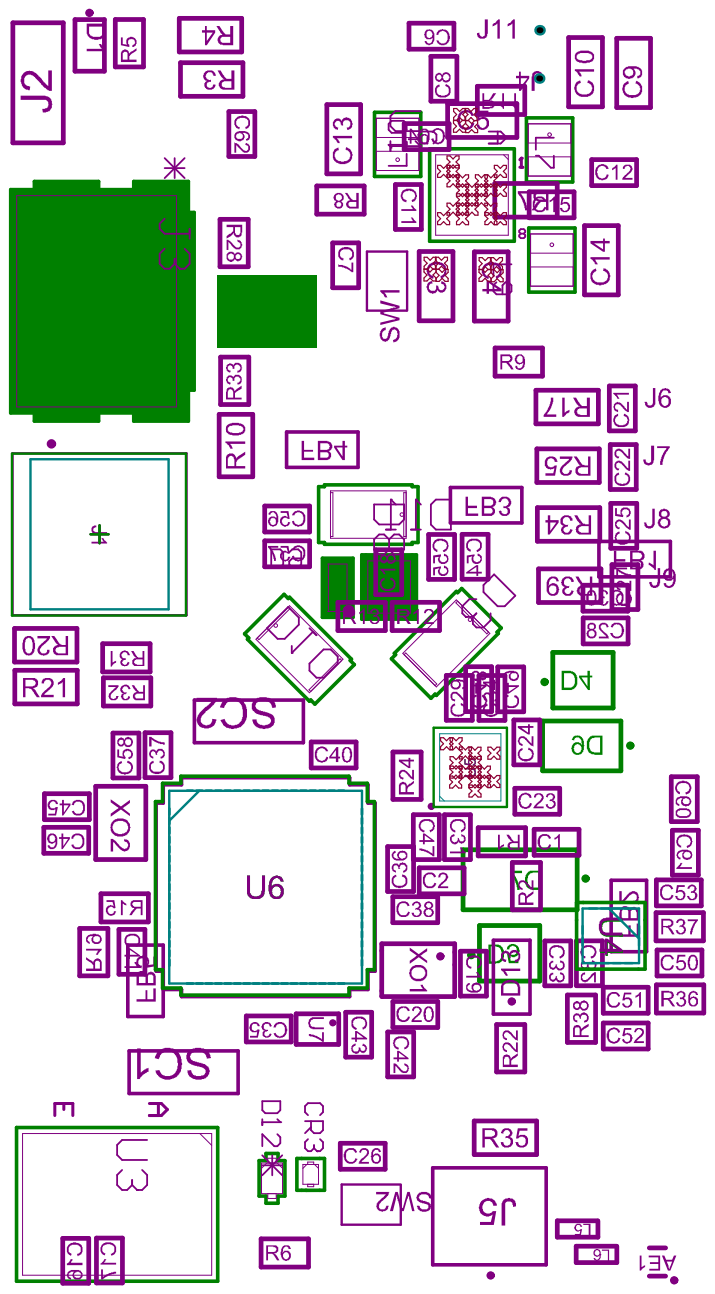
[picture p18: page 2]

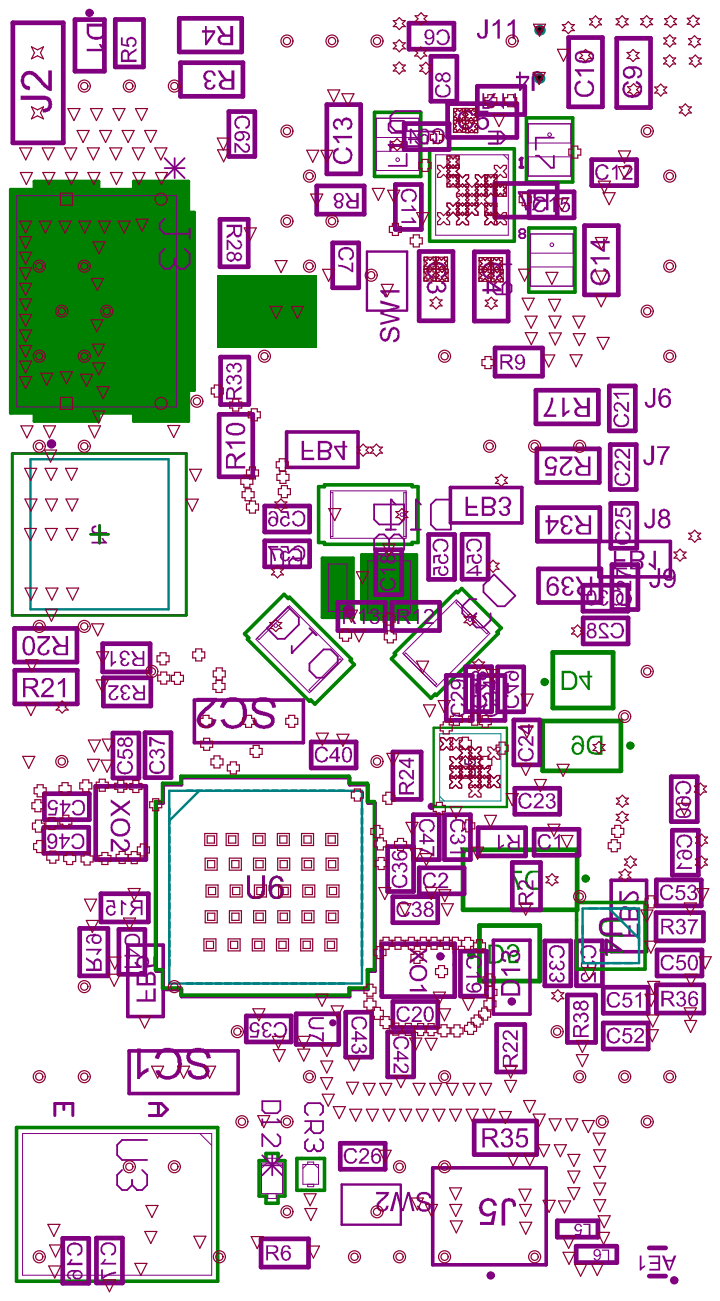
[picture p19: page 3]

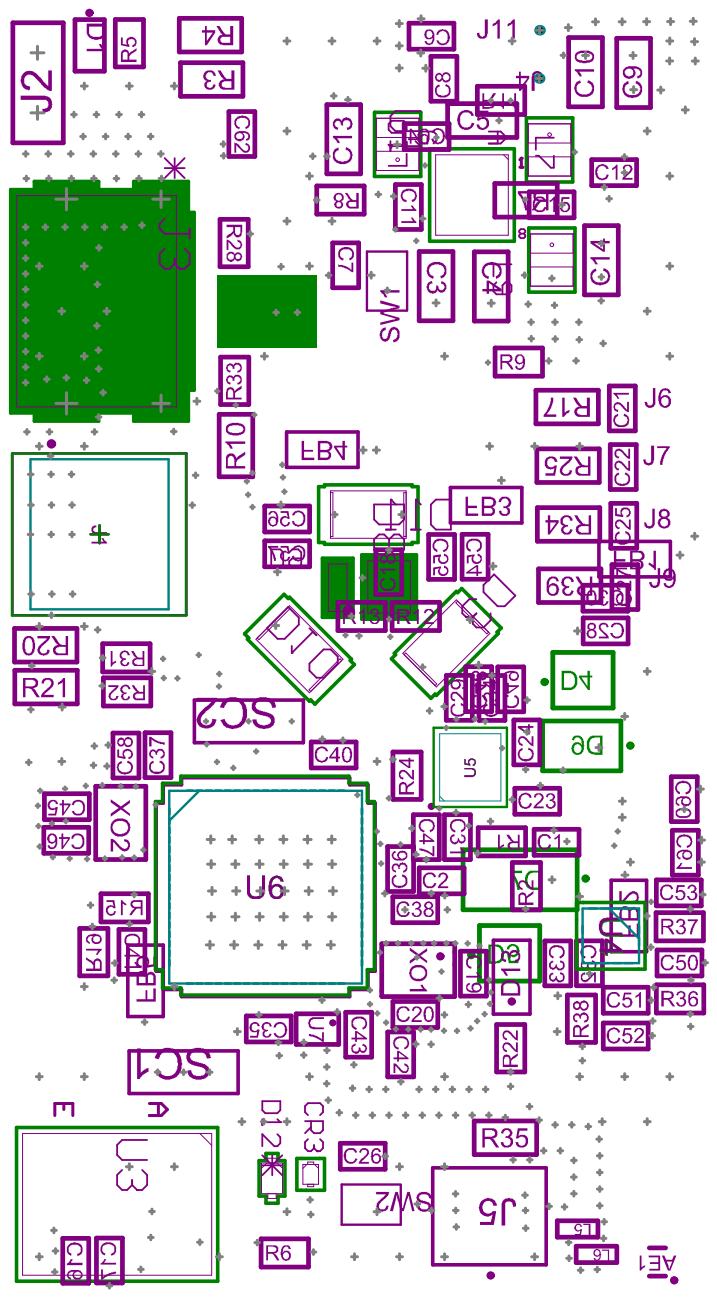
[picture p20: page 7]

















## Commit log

2026-01-23 updated AFE
    [01-multimodal-powersupply.SchDoc, 06-multimodal-analogfrontend.SchDoc, 07-multimodal-microcontroller.SchDoc, 09-multimodal-flash.SchDoc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]
2026-01-23 added accelerometer, started PMIC
    [01-multimodal-powersupply.SchDoc, 06-multimodal-analogfrontend.SchDoc, 09-multimodal-flash.SchDoc, multimodal.PcbLib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]
2026-01-23 commit all
    [12-multimodal-accelerometer.SchDoc, 13-multimodal-microcontroller-oscillators.SchDoc, 14-multimodal-microcontroller-switches.SchDoc, 15-multimodal-microcontrol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]
2026-01-23 name change
    [14-multimodal-microcontroller-switches.SchDoc]
2026-01-23 changing name
    [01-multimodal-powersupply.SchDoc, 14-multimodal-microcontroller-switches-display.SchDoc]
2026-01-23 added battery charging
    [02-multimodal-pmic.SchDoc, 06-multimodal-analogfrontend.SchDoc, 07-multimodal-microcontroller.SchDoc, 09-multimodal-flash.SchDoc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]
2026-01-23 power supply edits
    [01-multimodal-powersupply.SchDoc, 03-multimodal-battery-charger.SchDoc, 11-multimodal-combined-sensor.SchDoc]
2026-01-23 USB and SWD added
    [01-multimodal-powersupply.SchDoc]
2026-01-23 added RTC, sensors
    [01-multimodal-powersupply.SchDoc, 04-multimodal-flash.SchDoc, 05-multimodal-analogfrontend.SchDoc, 07-multimodal-microcontroller.SchDoc]
2026-01-23 uploading first draft
    [11-multimodal-accelerometer.SchDoc]
2026-01-23 added coversheet
    [01-multimodal-powersupply-connections.SchDoc, 02-multimodal-pmic.SchDoc, 03-multimodal-battery-charger.SchDoc, 04-multimodal-flash.SchDoc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]
2026-01-23 Added cover sheet
    [00-multimodal-coversheet.SchDoc]
2026-02-09 adding cover letter
    [00-multimodal-coversheet.SchDoc, 02-multimodal-pmic.SchDoc, 03-multimodal-battery-charger.SchDoc, 04-multimodal-flash.SchDoc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]
2026-02-09 cover letter + extra connections
    [01-multimodal-powersupply.SchDoc, 06-multimodal-analogfrontend-PPG.SchDoc, 07-multimodal-microcontroller.SchDoc, 08-multimodal-microcontroller-oscillators.SchD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]
2026-02-09 small adjustments
    [00-multimodal-coversheet.SchDoc, 07-multimodal-microcontroller.SchDoc, 13-multimodal-connections.SchDoc]
2026-02-10 finished the cover sheet
    [00-multimodal-coversheet.SchDoc, 01-multimodal-powersupply.SchDoc, 02-multimodal-pmic.SchDoc, 03-multimodal-battery-charger.SchDoc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]
2026-02-10 finished cover sheet, fixed component
    [Multimodal.PcbDoc]
2026-02-10 updated placement
    [Multimodal.PcbDoc, multimodal.PcbLib]
2026-02-27 placement + modified footprints + updated sheets
    [01-multimodal-powersupply.SchDoc, 02-multimodal-pmic.SchDoc, 03-multimodal-battery-charger.SchDoc, 04-multimodal-flash.SchDoc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]
2026-02-27 added 3D model
    [SOD-523_STM.step]
2026-03-03 routing updates
    [05-multimodal-analogfrontend.SchDoc, 08-multimodal-microcontroller-oscillators.SchDoc, 09-multimodal-microcontroller-switches-display.SchDoc, Multimodal.PcbDoc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]
2026-03-04 added diff pair notation to usb, added termination resistors to ADPD ECG channels + routing
    [05-multimodal-analogfrontend.SchDoc, 13-multimodal-connections.SchDoc, Multimodal.PcbDoc, multimodal.PcbLib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]
2026-03-08 schematic updates + routing
    [00-multimodal-coversheet.SchDoc, 01-multimodal-powersupply.SchDoc, 02-multimodal-pmic.SchDoc, 03-multimodal-battery-charger.SchDoc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]
2026-03-11 changed SWD connector
    [13-multimodal-connections.SchDoc, multimodal.PcbLib, multimodal.SchLib]
2026-03-11 changed connector
2026-03-14 routing + notes
    [03-multimodal-battery-charger.SchDoc, 10-multimodal-microcontroller-rf.SchDoc]
2026-03-27 changes regarding the pmic + connector changes + new vias
    [00-multimodal-coversheet.SchDoc, 01-multimodal-powersupply.SchDoc, 02-multimodal-pmic.SchDoc, 03-multimodal-battery-charger.SchDoc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]
2026-03-27 pmic updates
    [01-multimodal-powersupply.SchDoc, multimodal_hw_00.PrjPcb]
2026-03-31 routing + rf shield + 3d bodies
    [01-multimodal-powersupply.SchDoc, 05-multimodal-analogfrontend.SchDoc, 06-multimodal-analogfrontend-PPG.SchDoc, 07-multimodal-microcontroller.SchDoc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]
2026-03-31 changed sw, routing
    [01-multimodal-powersupply.SchDoc, 05-multimodal-analogfrontend.SchDoc, 07-multimodal-microcontroller.SchDoc, Multimodal.PcbDoc]
2026-04-01 removed extra esd, changed PMIC variant + edits on routing
    [01-multimodal-powersupply.SchDoc, 05-multimodal-analogfrontend.SchDoc, 13-multimodal-connections.SchDoc, Multimodal.PcbDoc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]
2026-04-02 updates guard ring & routing
    [05-multimodal-analogfrontend.SchDoc, 06-multimodal-analogfrontend-PPG.SchDoc, 07-multimodal-microcontroller.SchDoc, Multimodal.PcbDoc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]
2026-04-03 added extra test points, re-poured all polygons
    [01-multimodal-powersupply.SchDoc, Multimodal.PcbDoc, multimodal.PcbLib]
2026-04-03 generated 3D model for the board + min trace width 4 mil + usb impedance matching is done for the manufacturer stack-up sheet which is Huaqiu0661105-1080
    [Multimodal.PcbDoc, Multimodal.step]
2026-04-04 manufacturing files generated
    [Bill of Materials-multimodal_hw_00.xlsx, Multimodal.GBL, Multimodal.GBO, Multimodal.GBP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]
2026-04-04 updated job file
    [Multimodal.PcbDoc]
2026-04-04 3D model of component change
    [STP_61300211121_rev1.stp]
2026-04-11 made guard ring wider + added L3 guard ring for o2,co2 pds
    [Multimodal.PcbDoc, multimodal_hw_00.PrjPcb]
2026-04-11 NEXT PCB via change
    [Multimodal.PcbDoc]
2026-04-11 next pcb via change - i can do the same change for pcbway
    [Multimodal.PcbDoc]
2026-04-11 generated output files for NEXTPCB
    [Bill of Materials-multimodal_hw_00.xlsx, Multimodal.GBL, Multimodal.GBO, Multimodal.GBP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]
2026-04-11 changed the stack-up, trace widt etc for pcbway + generated files
    [Bill of Materials-multimodal_hw_00.xlsx, Multimodal.GBL, Multimodal.GBO, Multimodal.GBP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]
